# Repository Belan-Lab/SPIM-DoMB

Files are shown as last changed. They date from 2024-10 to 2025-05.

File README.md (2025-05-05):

Stand With Ukraine (https://stand-with-ukraine.pp.ua)

<p align="left">

</p>

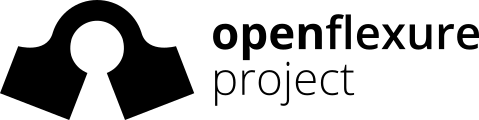
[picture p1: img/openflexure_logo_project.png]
OpenFlexure Project (https://gitlab.com/openflexure)


__SPIM for DoMB__
================

Selective Plane Illumination Microscope based on adaptations and modifications of original [openUC2](https://github.com/openUC2/UC2-GIT?tab=readme-ov-file) and [OpenFlexure Block Stage](https://gitlab.com/openflexure/openflexure-block-stage/) projects.

Department of Molecular Biophysics, Bogomoletz Institute of Physiology of NAS of Ukraine (Kyiv, Ukraine).

---

# Design notes

> [!TIP]
> Read more about the SPIM principles: 
>
> - [Selective Plane Illumination Microscopy](https://link.springer.com/chapter/10.1007/978-0-387-45524-2_37)
> - [openSPIM project](https://openspim.org/)
> - [Selective plane illumination microscopy techniques in developmental biology](https://journals.biologists.com/dev/article/136/12/1963/65234/Selective-plane-illumination-microscopy-techniques)
> - [Using tissue clearing and light sheet fluorescence microscopy for the three-dimensional analysis of sensory and sympathetic nerve endings that innervate bone and dental tissue of mice](https://onlinelibrary.wiley.com/doi/full/10.1002/cne.25582)

## Gaussian litgh-sheet
_Based on [Olarte et al., 2018](https://opg.optica.org/aop/fulltext.cfm?uri=aop-10-1-111&id=381035) and [Power and  Huisken, 2017](https://whttps://opg.optica.org/aop/fulltext.cfm?uri=aop-10-1-111&id=381035ww.nature.com/articles/nmeth.4224)._

__Schematic of the illumination and detection arm in a SPIM__ (_Olarte et al., 2018_)
<p align="center">
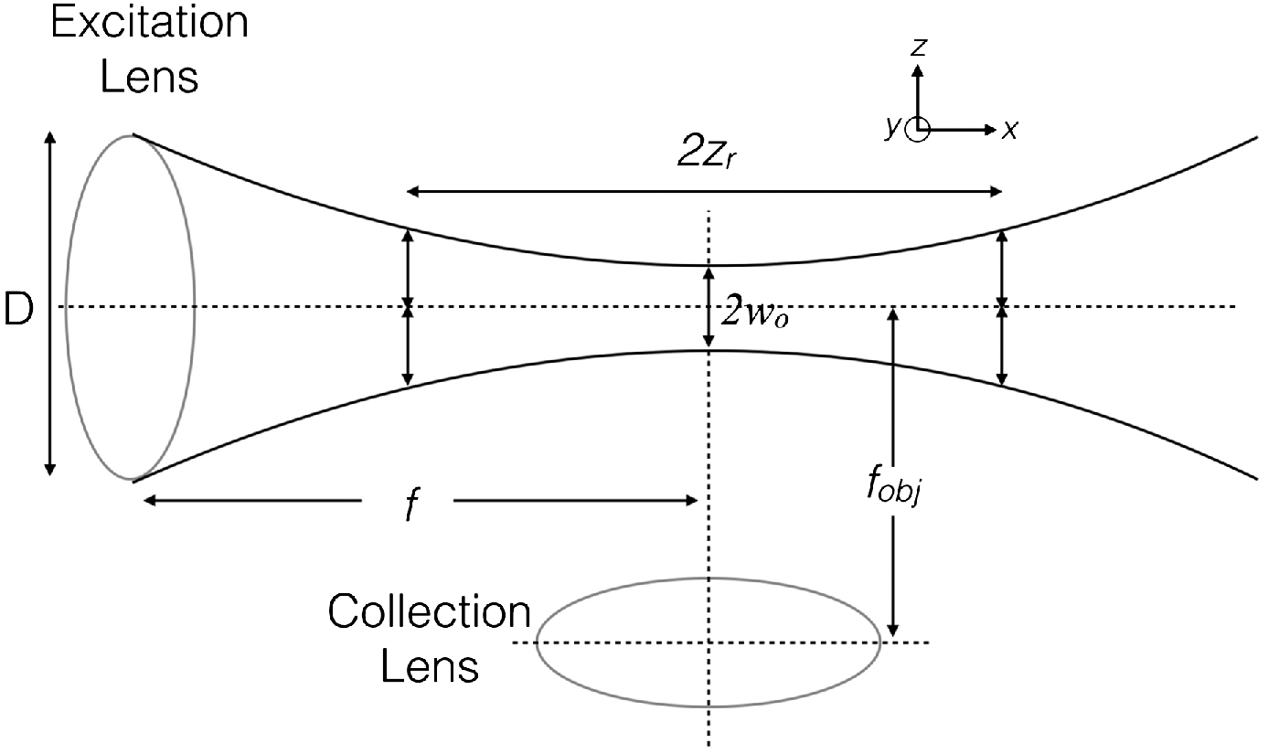
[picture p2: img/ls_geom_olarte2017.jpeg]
</a>
</p>

### Illumination arm
Light-sheet thickness (axial sectioning resolution): 

```math
l_z = 2w_0 = 2 \frac{n \cdot \lambda_{ex.}}{\pi \cdot NA_{ex.}}
```

Light-sheet length (field of view/FOV):

```math
l_x = 2z_r = 2 \frac{\pi \cdot w_0^2}{\lambda_{ex.}} = 2 \frac{n^2 \cdot \lambda_{ex.}}{\pi \cdot NA_{ex.}^2}
```

### Detection arm
Lateral resolution (Rayleigh criterion):

```math
d_{xy} = \frac{0.61 \cdot \lambda_{det.}}{NA_{det.}}
```

Axial resolution (depth of field/DOF):

```math
d_z = \frac{n \cdot \lambda_{det.}}{NA_{det.}^2}
```

# Samples and desired characteristics

__NB: is 10x NA 0.25 FN 22 enough?__

## Sciatic nerve
- Nerve diameter: 1.5-2 mm
- Nerve length: 5-20 mm
- A-fiber diameter: 1.5 - 10 um 
- C-fiber diameter: 0.5 - 2 um
- Minimal vessel diameter

## Scaffolds
_In progress_

# Relation of components and parameters
## Objectives

| Model                           | Olympus PlaN | Olympus UPlanFl Ph. 1 |
| ------------------------------- | ------------ | --------------------- |
| Magnification (M)               | 10x          | 10x                   |
| Numerical aperture (NA)         | 0.25         | 0.3                   |
| Working distance (WD)           | 10.6 mm      | 10 mm                 |
| Focal distance (F)              | 18 mm        | 18 mm                 |
| Back focal plane distance (BFP) | N/A          | -19.1 mm              |
| Field number (FN)               | 22           | 26.5 mm               |
| Lateral resolution              | 1.34 μm      | 1.12 μm               |
| Parafocal distance (PD)         | 45 mm        | 65 mm                 |
| Exit pupil diameter (EP)        | 9 mm         | 10.8 mm               |

## Cameras

| Model           | FLIR Grasshopper 3     | Basler ace 2 R       |
| --------------- | ---------------------- | -------------------- |
| ID              | GS3-U3-23S6M-C         | a2A5320-23umPRO      |
| Sensor          | Sony IMX174 (CMOS)     | Sony IMX542 (CMOS)   |
| Sensor size     | 11.25x7.03 mm (1/1.2") | 14.58x8.31 mm (1.1") |
| Sensor diagonal | 13.4 mm                | 16.78 mm             |
| Pixels (HxV)    | 1920x1200 (2.3 Mpx)    | 5320x3032 (16.1 Mpx) |
| Pixel size      | 5.86x5.85 μm           | 2.74x2.74 μm         |
| Frame rate      | up to 162 fps          | up to 24 fps         |

---

# T-SPIM 
Here will be construction notes for the next project, T-SPIM extension of DoMB-SPIM.

## Design overview, V0

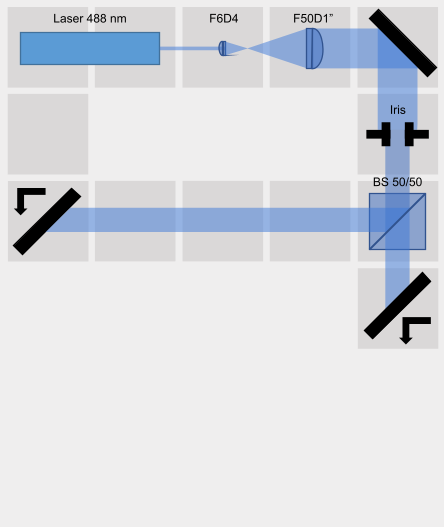
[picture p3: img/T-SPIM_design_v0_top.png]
| Top layer        |     |
| :--------------: | :----------------------------------: |
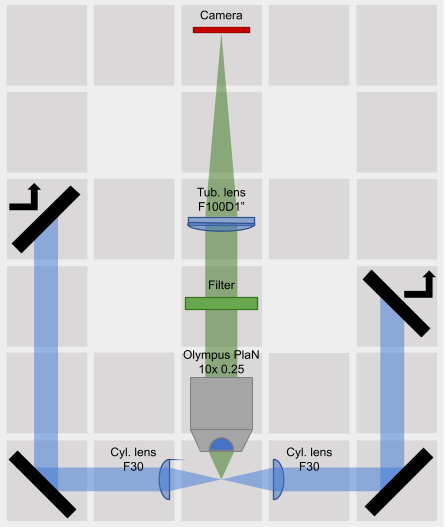
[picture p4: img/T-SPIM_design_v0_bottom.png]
| __Bottom layer__ |  |

---

# L-SPIM

## Microscope configuration
<p align="center">
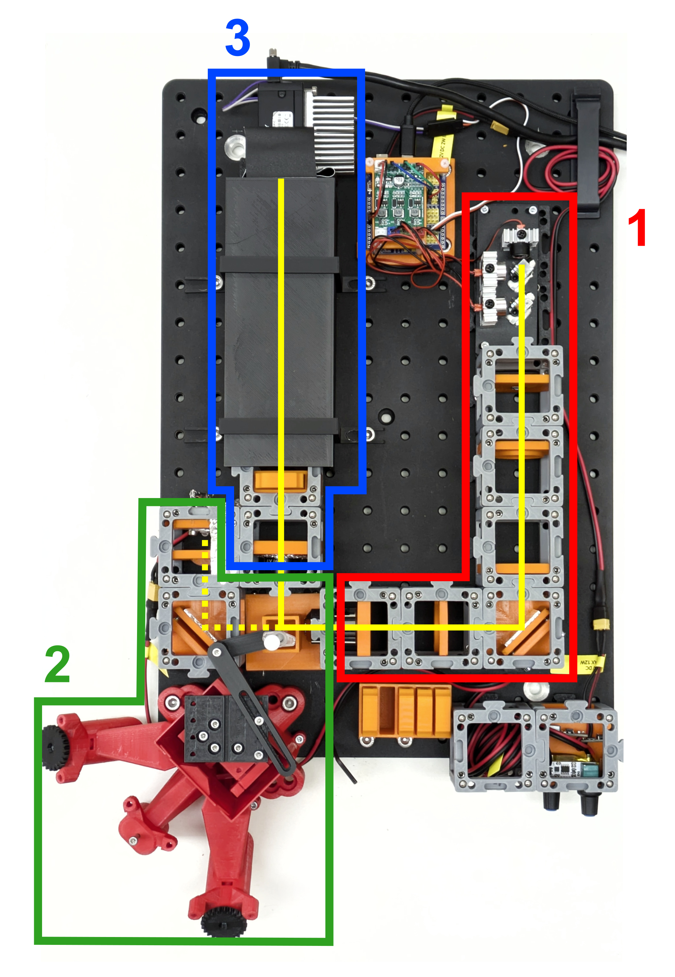
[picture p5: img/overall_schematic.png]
</a>
</p>

The microscope consists of three main parts: (__1__) excitation light path with a light source, light source control board, and light sheet collimation system, (__2__) sample handling part which includes a sample chamber with modified OpenFlexure Block Stage and side illumination system, and (__3__) detection light path with emission filter, tube lens, and industrial-grade CMOS camera ([FLIR Grasshopper 3](https://www.edmundoptics.com/p/gs3-u3-23s6m-c-112-grasshopper-usb-30-monochrome-camera/30859/?srsltid=AfmBOor05Spkup9nlj1Yhpo8lcCk5ABTsBXECeMxt9GTolSTdF2UEIqc) in our case). A solid yellow line indicates the excitation and detection light path, and a dashed yellow line indicates the brightfield side-illumination light path. 

The whole setup is based on on-shelf parts and low-cost solutions with minimal additional modifications. For all 3D-printed parts, parametric openSCAD models were provided for flexible modification and customization without a great entry threshold.  

This system is under strong development, so check for future updates.

## First results

__Light sheet configuration__
 Light sheet top view | Light sheet side view | Light sheet focus point view 
:-------------------------:|:-------------------------:|:-------------------------:
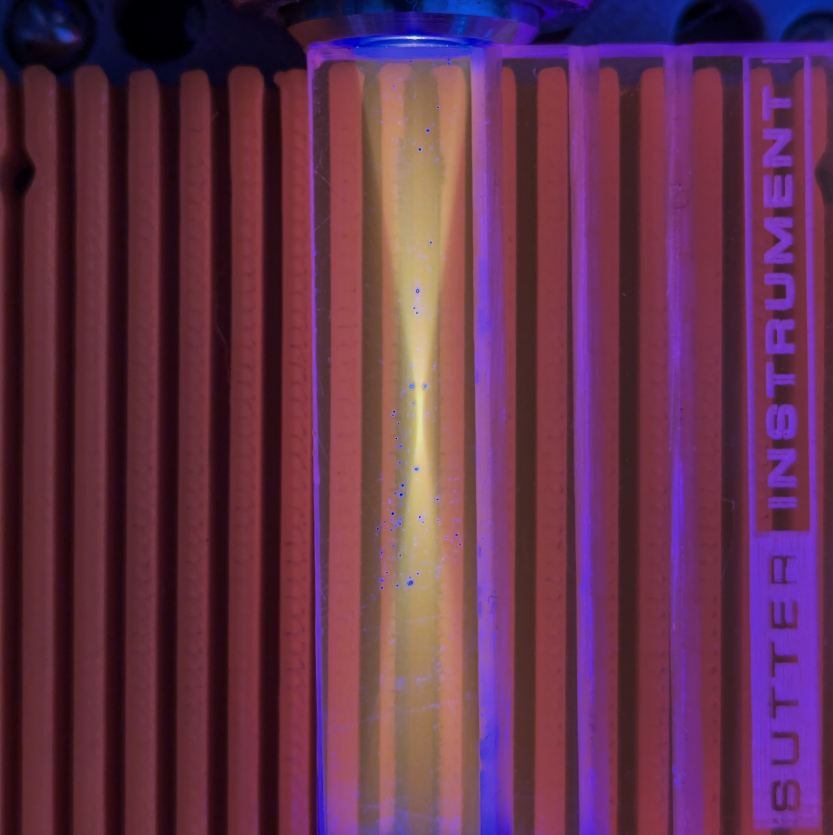
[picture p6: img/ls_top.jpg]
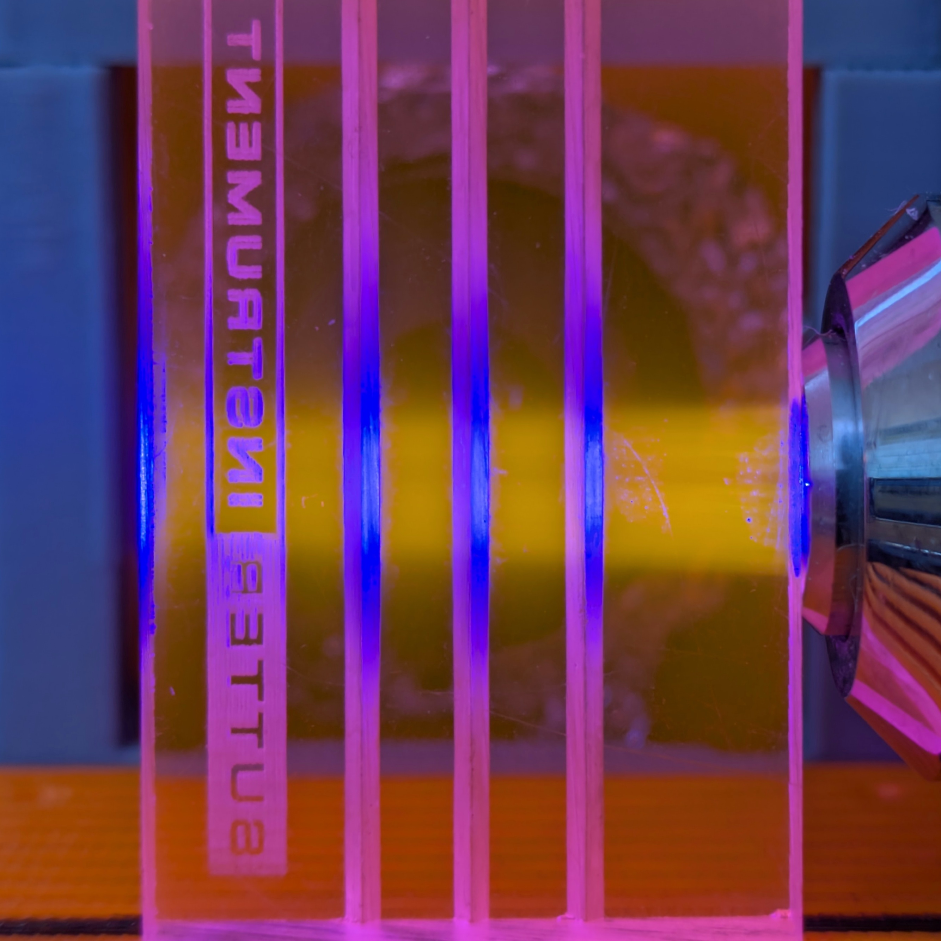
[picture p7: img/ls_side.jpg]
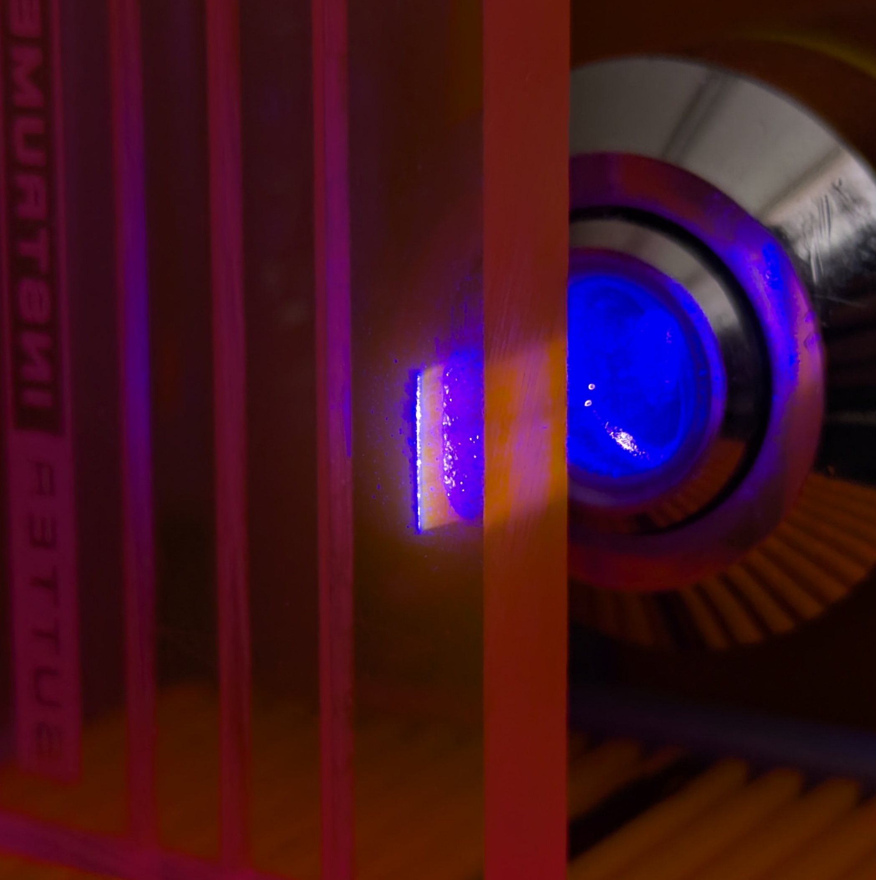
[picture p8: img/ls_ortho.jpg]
||  

__Z-stack and reconstruction of whole mount staining of vessels endothelial cells in the sciatic nerve__

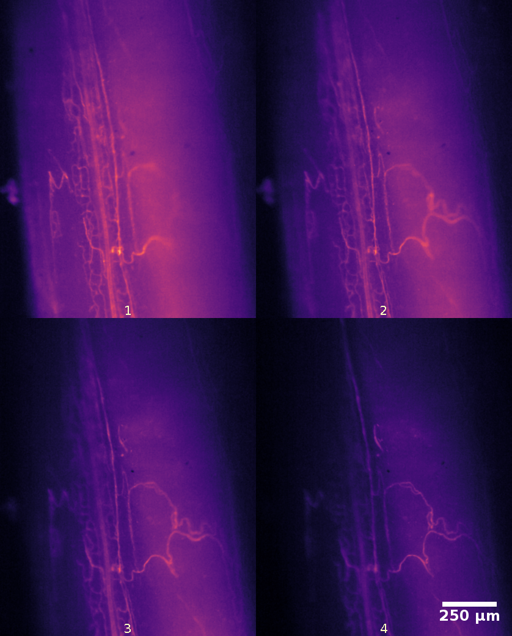
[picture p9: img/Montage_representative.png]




## Construction notes
General materials and parts needed for printing and assembling:

| Part                               | #     | Cost/unit | Link                                                         |
| ---------------------------------- | ----- | --------- | ------------------------------------------------------------ |
| Optical breadboard 30x45 cm        | 1x    | $135      | [AliExpress](https://a.aliexpress.com/_EwQ40qd)              |
| M3x12 DIN912 screw                 | ~200x | ~$8 / 200 | Metalvis                                                     |
| M6x12 DIN912 screw                 | ~30x  | ~$6 / 30  | Metalvis                                                     |
| M6x12 DIN912 screw                 | ~10x  | ~$1 / 10  | Metalvis                                                     |
| M5x8 DIN914 screw                  | ~150x | ~$5 / 150 | Metalvis                                                     |
| 1.75 mm PLA filament (750 g/pack)  | 2x    | $11       | [Monofilament](https://monofilament.com.ua/ua/products/standartnye-materialy/pla/pla-cvetlo-seryj-o1-75mm-ves0-75kg) |
| 1.75 mm ABS+ filament (750 g/pack) | 1.5x  | $10.85    | [Monofilament](https://monofilament.com.ua/ua/products/standartnye-materialy/abs-plus/abs-plus-oranzhevyj) |
| __Total__                          |       | __~$200__ |                                                              |

## 1. Excitation light path

<p align="center">
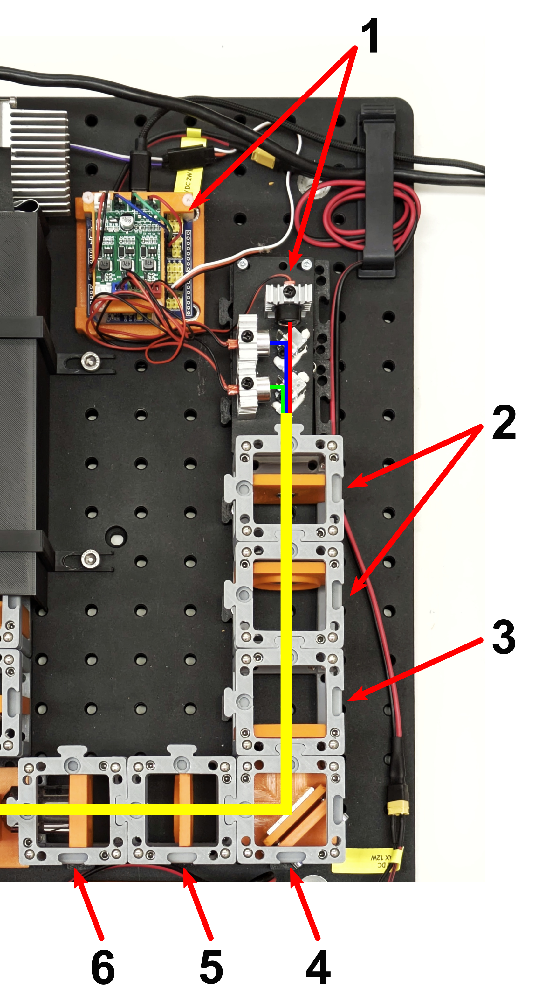
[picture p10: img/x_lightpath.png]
</a>
</p>

1. [RGB lasers module and lasers trigger board](#rgb-laser-module-v0)
2. ~12x beam expander: iPhone 4S lens F3.85 and F50 lens
3. Cylinrical lens F30
4. 45° kinematic mirror
5. Focusing lens F50
6. Projection objective 10x NA 0.25

| Part                                      | #    | Cost/unit | Link                                            |
| ----------------------------------------- | ---- | --------- | ----------------------------------------------- |
| [RGB lasers module](#rgb-laser-module-v0) | 1x   | $23       |                                                 |
| iPhone 4S lens F3.85                      | 1x   | -         |                                                 |
| F50 D30 lens                              | 2x   | $0.68     | [AliExpress](https://a.aliexpress.com/_ExOjTDP) |
| F30 20x22 mm cylindrical lens             | 1x   | $10.54    | [AliExpress](https://a.aliexpress.com/_EuDzlJ3) |
| Fron surface mirror 30x30 mm              | 1x   | $1.46     | [AliExpress](https://a.aliexpress.com/_EHn0u2l) |
| 10x NA 0.25 infinity corrected objective  | 1x   | $15.54    | [AliExpress](https://a.aliexpress.com/_ExDrPj7) |
| __Total__                                 |      | __~$52__  |                                                 |

## 2. Sample handling

<p align="center">
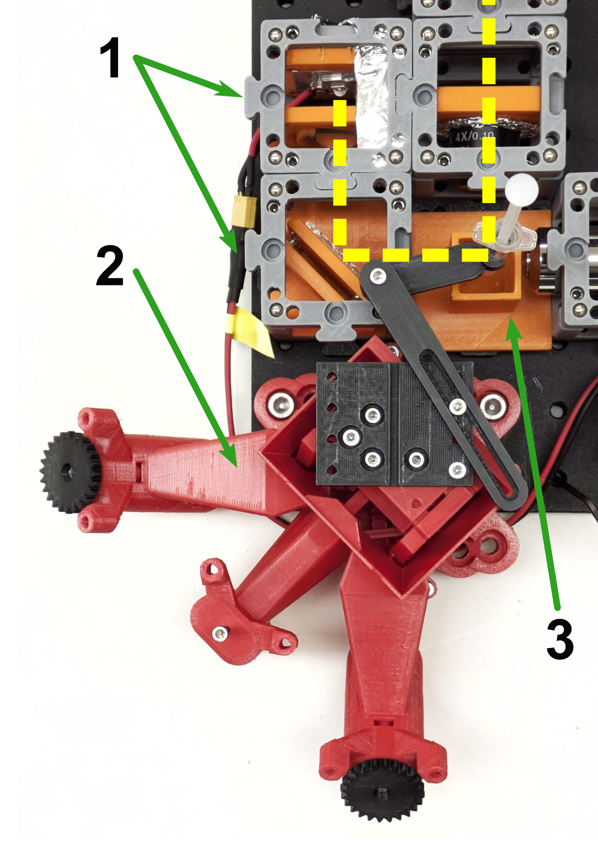
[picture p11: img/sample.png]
</a>
</p>

1. [White LED 3.3V 10W](#led-and-power-cube-v0) and 45° kinematic mirror
2. [OpenFlexure Block Stage with sample holder](#openflexure-block-stage-and-sample-holder)
3. [Sample chamber](#sample-chamber-v0)

| Part                                         | #    | Cost/unit | Link                                            |
| -------------------------------------------- | ---- | --------- | ----------------------------------------------- |
| [LED and power cube](#led-and-power-cube-v0) | 1x   | $12.68    |                                                 |
| Fron surface mirror 30x30 mm                 | 1x   | $1.46     | [AliExpress](https://a.aliexpress.com/_EHn0u2l) |
| __Total__                                    |      | __~$14__  |                                                 |

## 3. Detection light path

<p align="center">
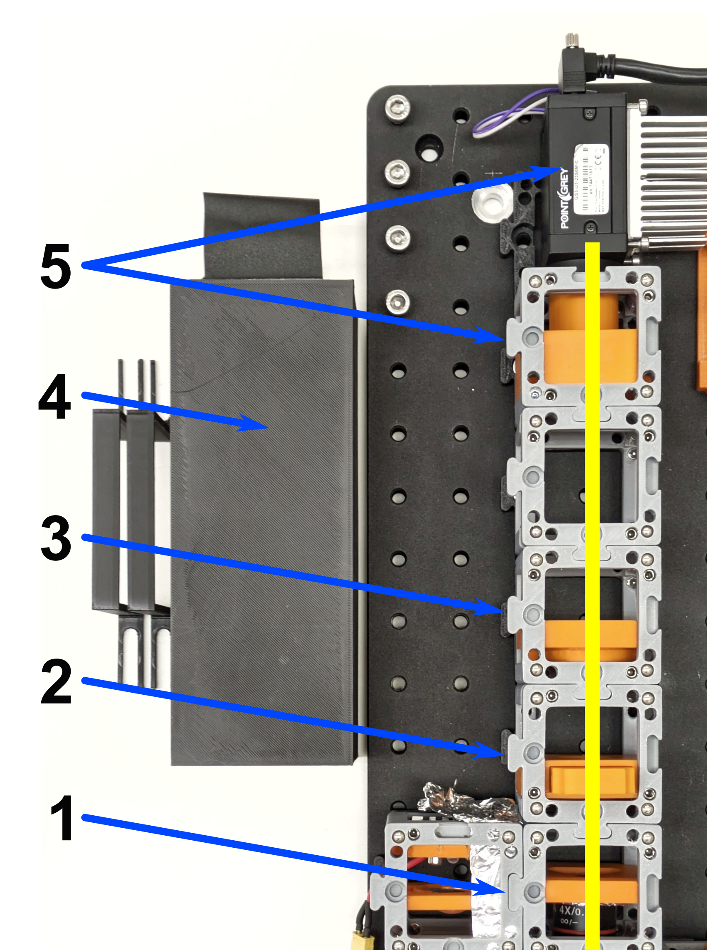
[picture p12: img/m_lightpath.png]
</a>
</p>

1. Objective 4x NA 0.1
2. [Emission filter holder](#25-mm-filter-holder-v1)
3. Tube lens ~F180
4. Light protection enclosure
5. CMOS camera and [C-mount cube](#c-mount-adapter)

| Part                                   | #    | Cost/unit                                  | Link                                                         |
| -------------------------------------- | ---- | ------------------------------------------ | ------------------------------------------------------------ |
| 4x NA 0.1 infinity corrected objective | 1x   | $13.25                                     | [AliExpress](https://a.aliexpress.com/_ExDrPj7)              |
| 25 mm emission filter                  | 1x   | discontinued old filter set, but new >$300 |                                                              |
| F~180 D40 lens                         | 1x   | from old stereomicroscope                  |                                                              |
| FLIR Grasshopper 3                     | 1x   | $1179                                      | [Edmund Optics](https://www.edmundoptics.com/p/gs3-u3-23s6m-c-112-grasshopper-usb-30-monochrome-camera/30859/?srsltid=AfmBOor05Spkup9nlj1Yhpo8lcCk5ABTsBXECeMxt9GTolSTdF2UEIqc) |
| __Total__                              |      | __~$1195__                                 |                                                              |

> [!IMPORTANT]
>
> The cost of the entire microscope, excluding the CMOS camera and emission filters set, was less than $300. A possible alternative for expensive emission filters may be industrial-grade filters for multimedia projector systems, but with a minimal selection of possible passbands. I also recommend paying attention to other manufacturers of industrial monochrome cameras: [Allied Vision](https://www.alliedvision.com/en/products/camera-series/alvium-1800-u/), [Basler](https://www.baslerweb.com/en/cameras/?srsltid=AfmBOooR76UWs6U6YJbZBzX9LeqmtPnLls9piX8MenW-n_NOVcxJU0dT), [Daheng](https://en.daheng-imaging.com/list-2-1.html).

---

# Cubes and modules
## OpenFlexure Block Stage for SPIM

Active development of OpenFlexure Block Stage adaptation continues on a separate [repository](https://github.com/Belan-Lab/OpenFlexure-XYZR).

__Block Stage side view__
<p align="center">
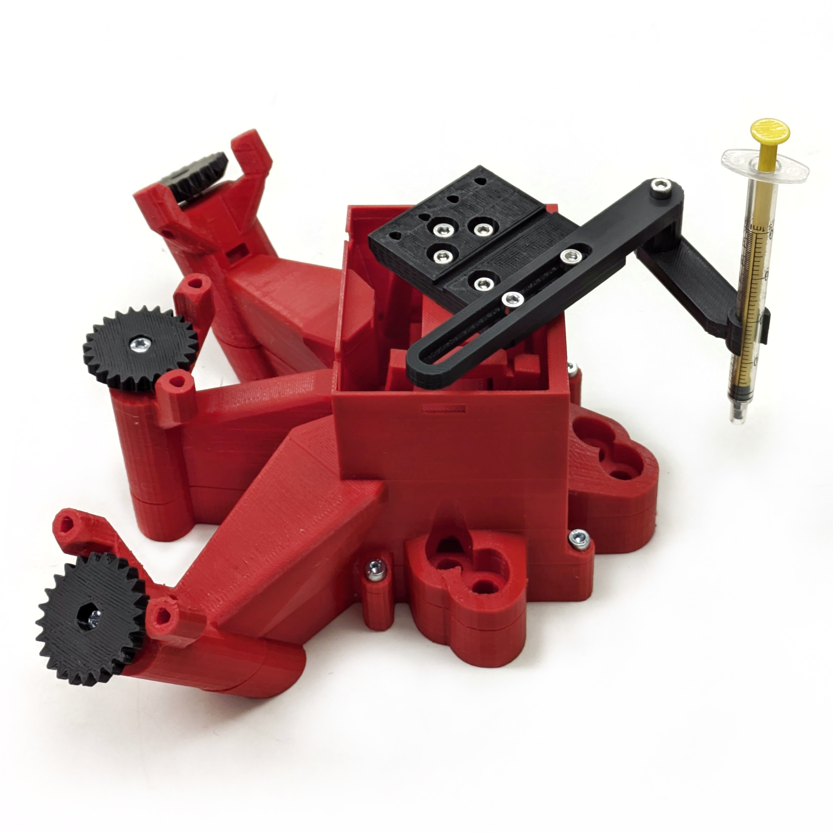
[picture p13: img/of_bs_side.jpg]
</a>
</p>

## C-mount adapter
Parametric model of a cube insert with C-mount thread (_c-mount_insert_v0.scad_).

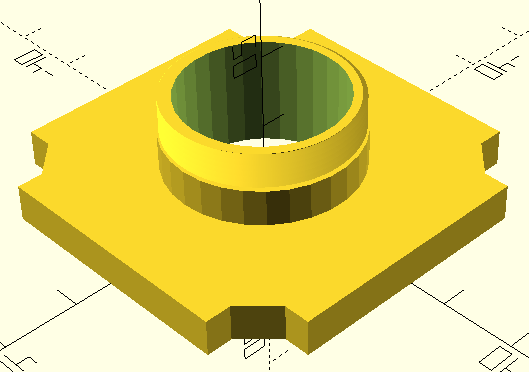
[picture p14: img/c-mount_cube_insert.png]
Model         | 
:-------------------------:|:-------------------------:
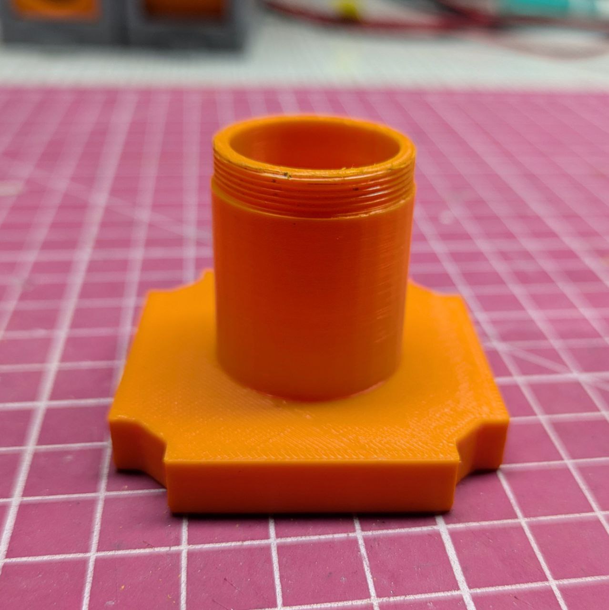
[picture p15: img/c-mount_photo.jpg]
__Printed long insert__ | 
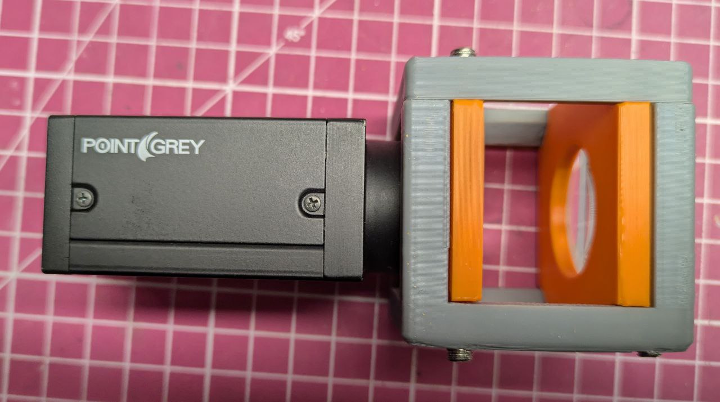
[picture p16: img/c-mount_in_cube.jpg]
__Installed insert__| 

##  LED and power cube V0
Parametric model of a cube insert with two LED dimmers and 12V output with type-C Power Delivery input (_led_power_insert_v0.scad_).

__Model__

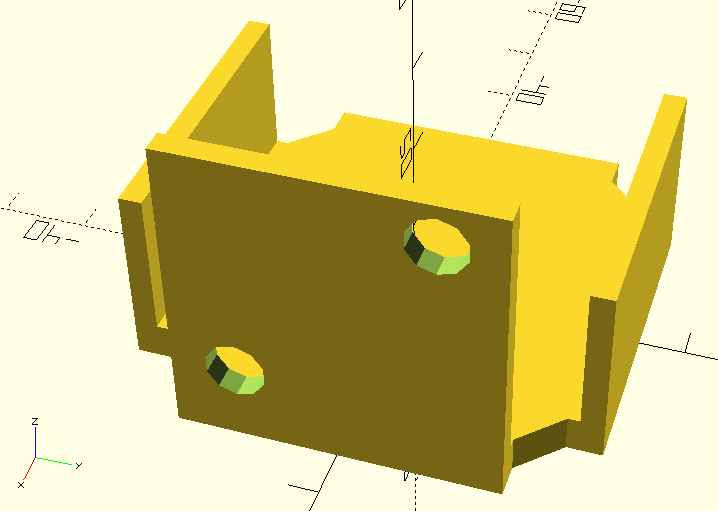
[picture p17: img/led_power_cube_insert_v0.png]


Part|#|Cost/unit|Link
-|-|-|-
LED dimmer | 2x | $2.72   | [AliExpress](https://a.aliexpress.com/_EuX3DTP) 
PD decoy module 12V | 1x | $0.44   | [AliExpress](https://a.aliexpress.com/_Ezeg4Hf) 
Mini560 Pro Step Down to 3.3V| 1x | $0.81  | [AliExpress](https://a.aliexpress.com/_EJQFP5x) 
White LED 10W 3.3V (XML2) | 1x | $1.29  | [AliExpress](https://a.aliexpress.com/_EHBMyXT) 
460 nm LED 3W 3.3V | 1x | $0.2 | [AliExpress](https://a.aliexpress.com/_EI94HWN)
Acrilic LED lens, F22 D20.8 | 2x | $1.35 | [AliExpress](https://a.aliexpress.com/_EHJOUo1) 
XT30 connector | 3x | $0.6  | [arduino.ua](https://arduino.ua/prod5276-xt30-konnektor-para-dlya-podklucheniya-li-po-li-ion-akkymylyatorov)
__Total__ |  | __$12.68__ | 

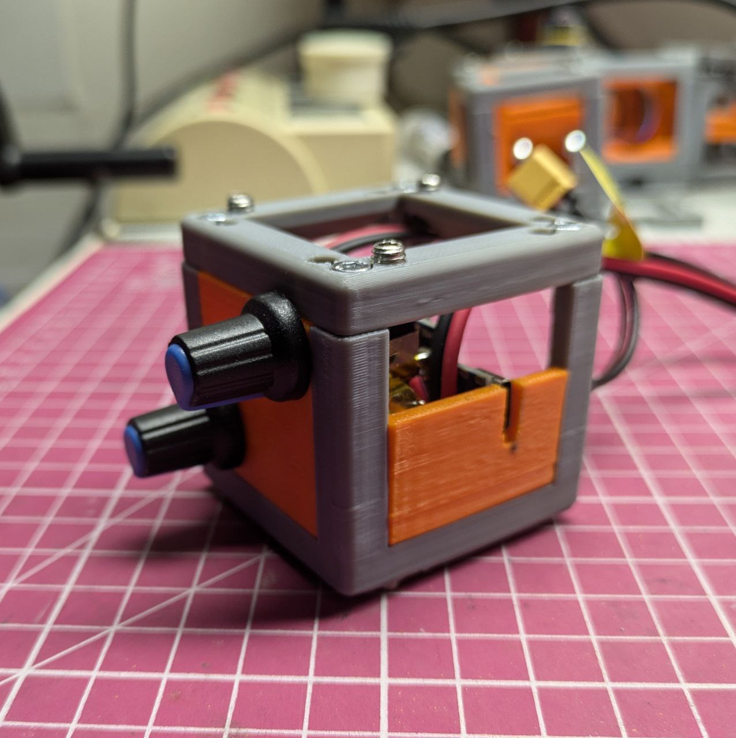
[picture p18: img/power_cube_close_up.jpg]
Assembled power cube            | 
:-------------------------:|:-------------------------:
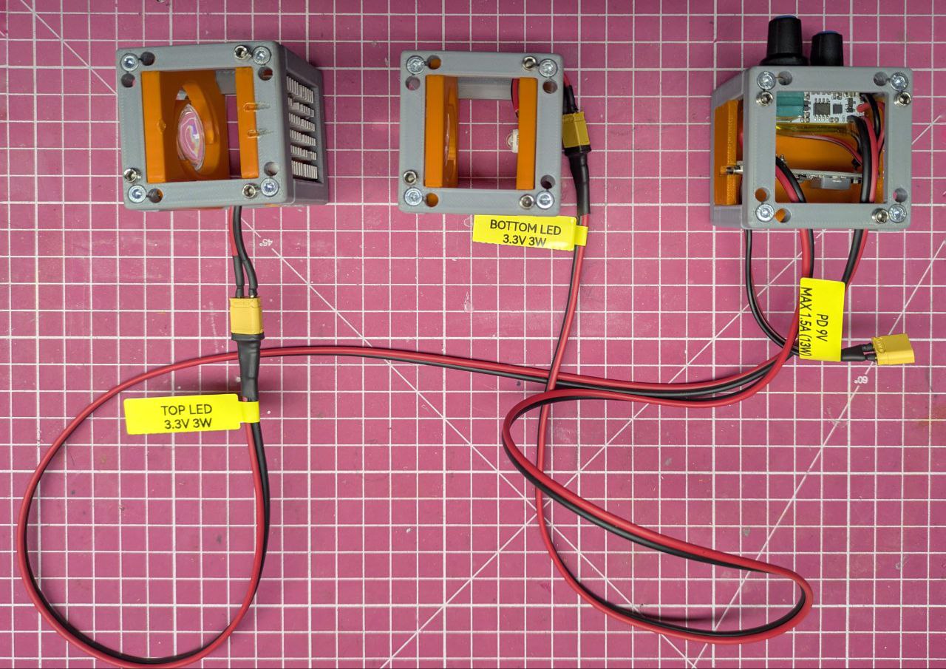
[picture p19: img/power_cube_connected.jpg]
__Power cube with two LED cubes__ | 

__White 10W LED cube with radiator from northbridge__

Front view            |  Back view
:-------------------------:|:-------------------------:
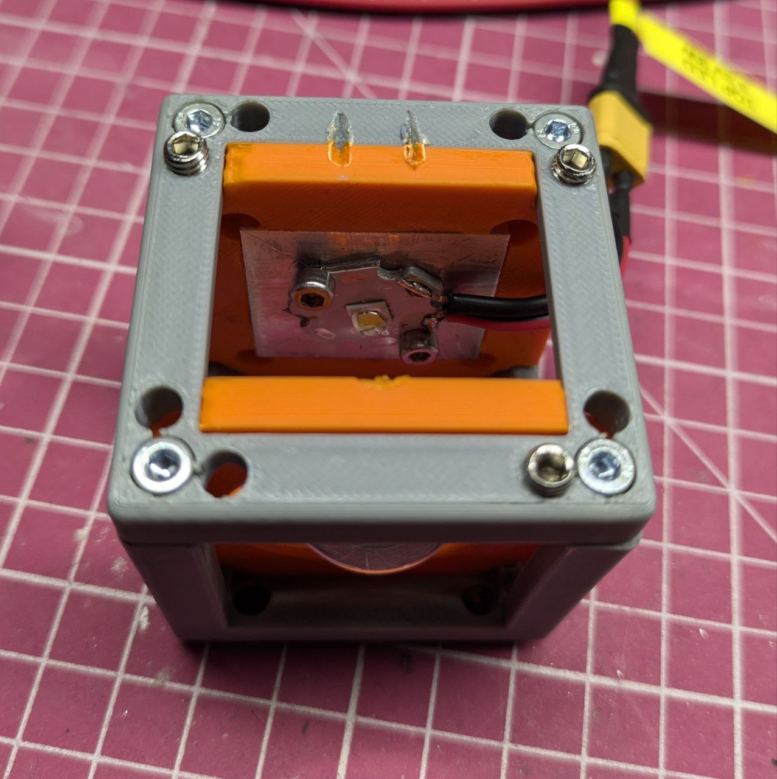
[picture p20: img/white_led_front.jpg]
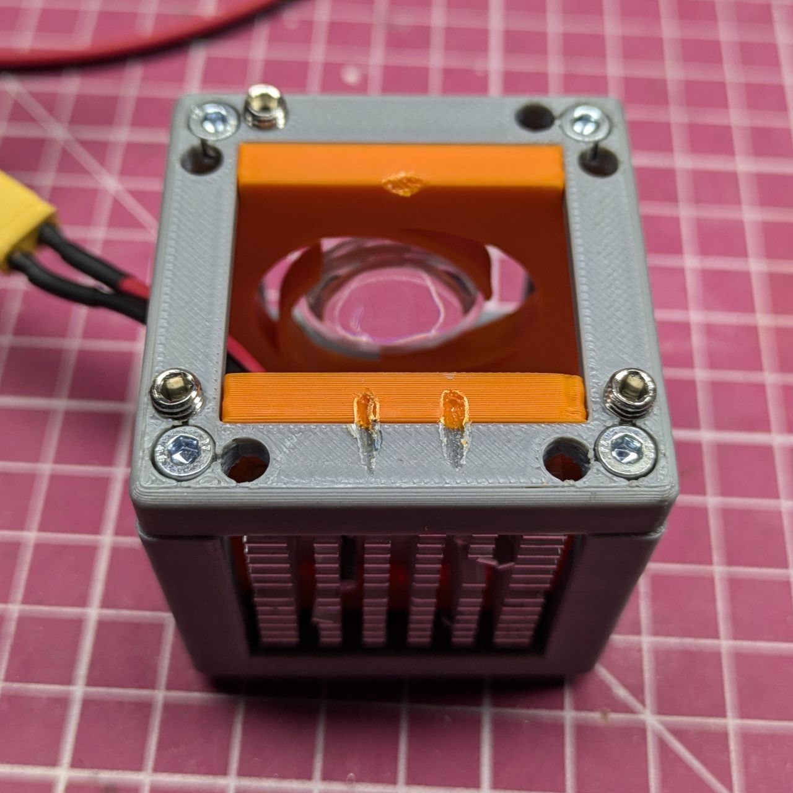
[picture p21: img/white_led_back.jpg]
 | 

## 25 mm filter holder V1
Sliding holder for standard 25 mm optical filters. The storage box for filter holders has mounting holes for standard M6 25mm spacing optical board.

__Model__

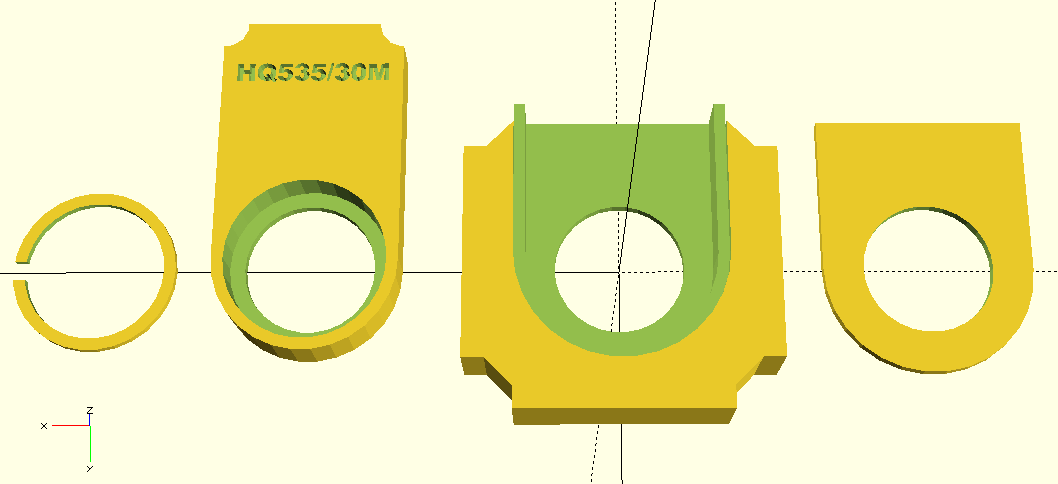
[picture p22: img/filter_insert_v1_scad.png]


Assembled filter cube             | Filter cube with filter holders and holders storage box 
:-------------------------:|:-------------------------:
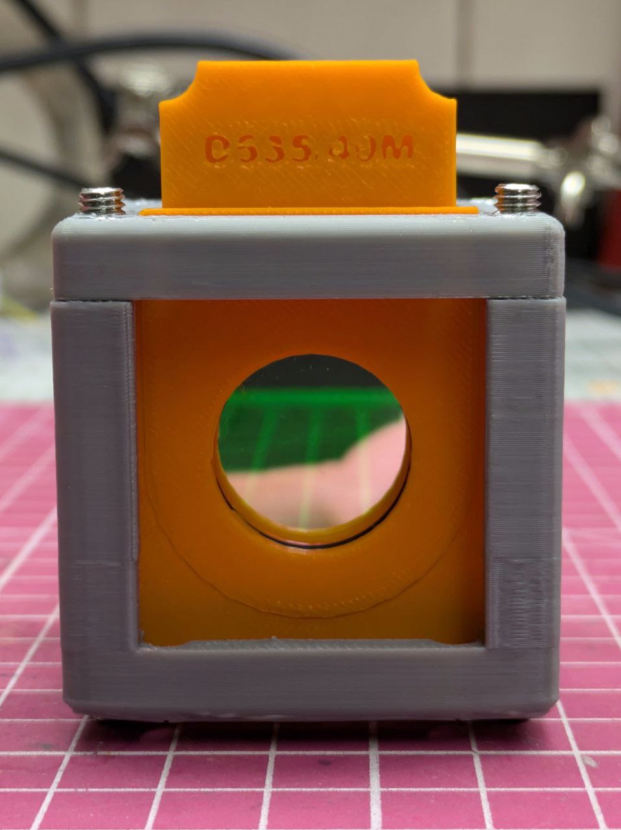
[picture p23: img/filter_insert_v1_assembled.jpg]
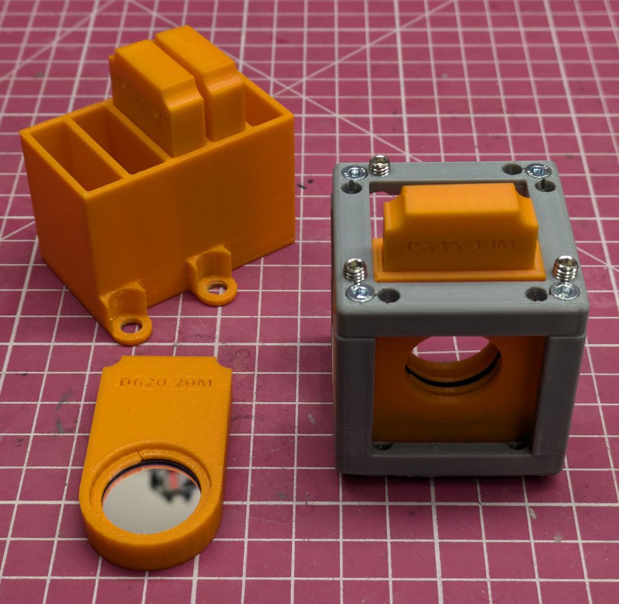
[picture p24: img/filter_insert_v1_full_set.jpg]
 | 

## Sample chamber V0
Sample chamber with three glass walls, as chamber windows was used 18 mm diameter 0.18 mm thickness coverslips mounted on silicone sealant.

Model           |  Assembled chamber
:-------------------------:|:-------------------------:
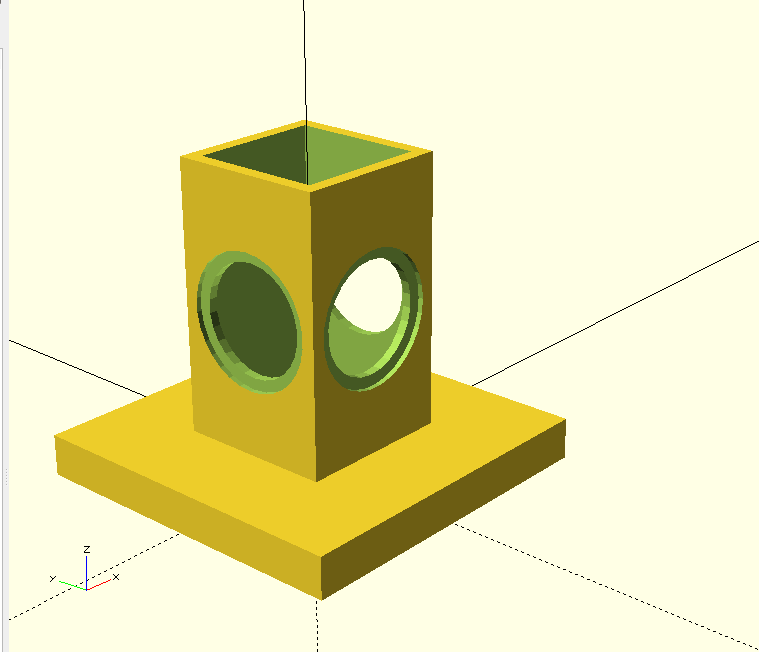
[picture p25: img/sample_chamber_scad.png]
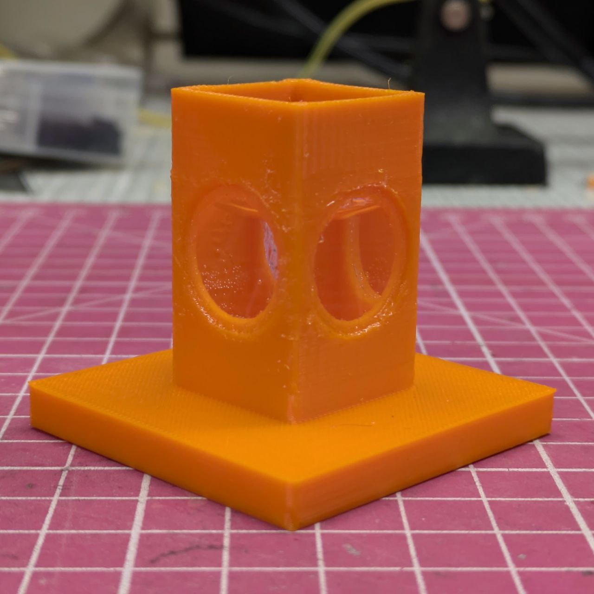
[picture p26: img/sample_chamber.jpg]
 | 

## Servo stage V1
The holder was adapted to install a plastic photometric cuvette for sample mounting.

__Model__
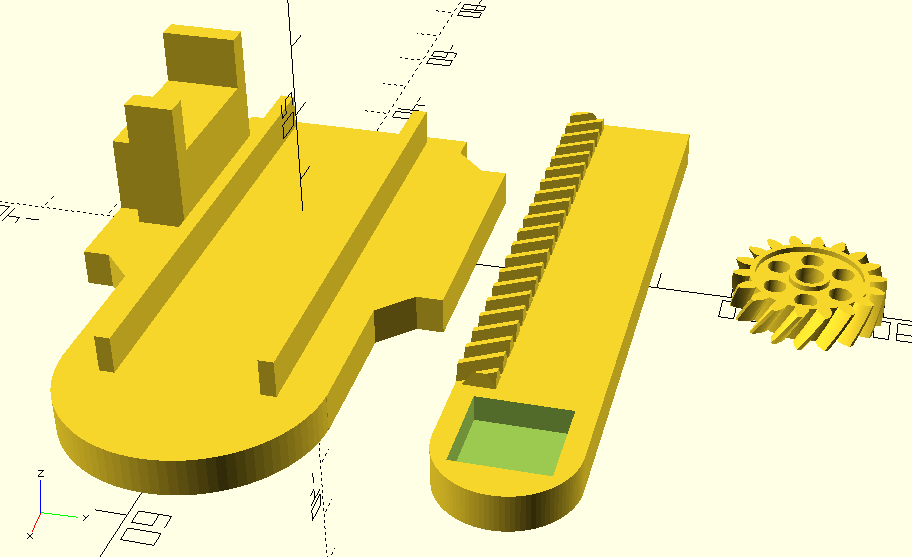
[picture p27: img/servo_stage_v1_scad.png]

_Includes openSCAD library "Bibliothek für Evolventen-Zahnräder, Schnecken und Zahnstangen" (gear.scad)_

__Assembled cube__

Top view            |  Side view
:-------------------------:|:-------------------------:
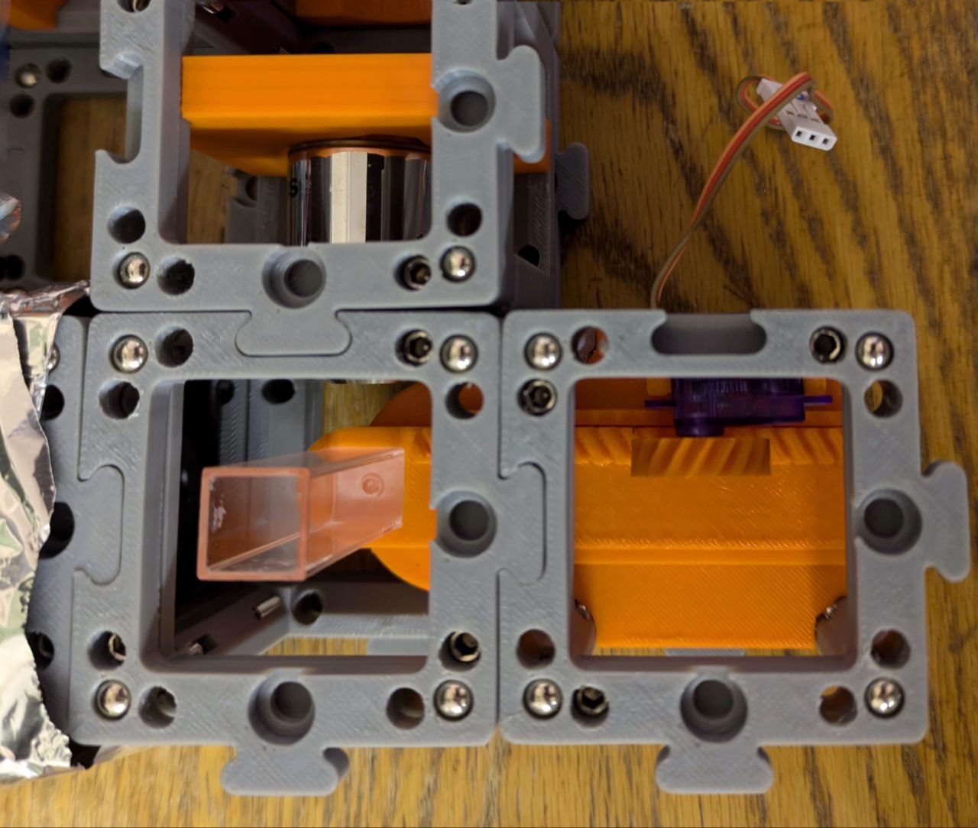
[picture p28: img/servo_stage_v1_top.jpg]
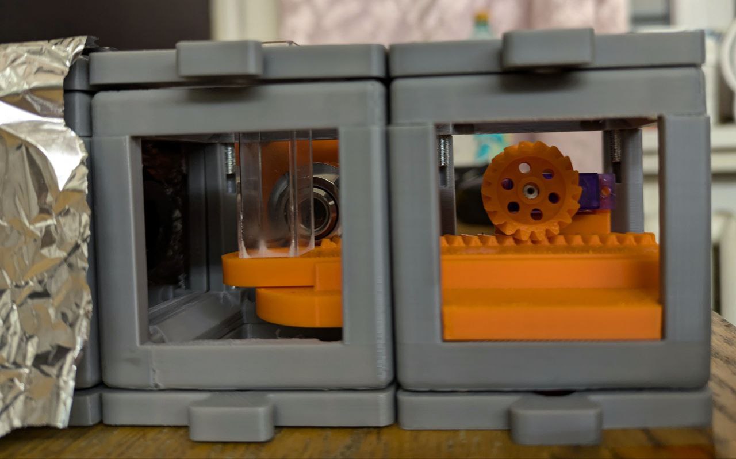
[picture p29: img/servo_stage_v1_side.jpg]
 | 

## 5X Laser beam expander V0

__Model__

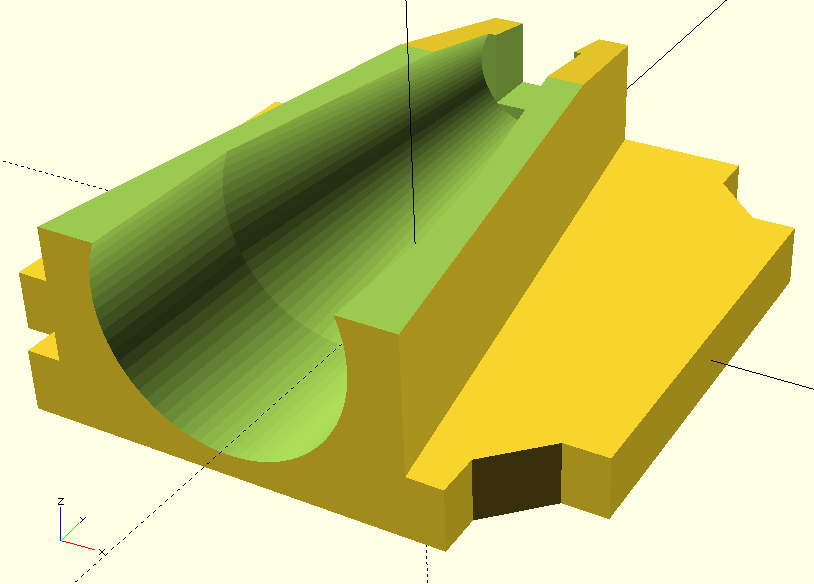
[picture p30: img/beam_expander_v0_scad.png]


Part|#|Cost/unit|Link
-|-|-|-
Acrilic LED lens, F22 D20.8 | 1x | $1.35 | [AliExpress](https://a.aliexpress.com/_EHJOUo1) 
iPhone 4S lens, F3.85 | 1x |  -  |  

## RGB lasers module V0

Module for mounting and control with Arduino of the RGB laser LED module.

Part|#|Cost/unit|Link
-|-|-|-
RGB laser module | 1x | $19.5 | [AliExpress](https://a.aliexpress.com/_EHowiiN)
Arduino Nano compatible board | 1x | $2.13 | [AliExpress](https://a.aliexpress.com/_EwrjzyD) 
Arduino Nano expansion board | 1x | $0.94 | [AliExpress](https://a.aliexpress.com/_EyNqegd) 
PD decoy module 12V | 1x | $0.44 | [AliExpress](https://a.aliexpress.com/_Ezeg4Hf) 
__Total__ |  | __$23__ |  

__RGB laser trigger board modification__

The original diode bridge on the RBG laser trigger board (circled in red) was replaced with two jumpers for the DC power supply only, and the original trigger connectors were replaced with 2.54 mm pin headers.

Original board             |  Modified board
:-------------------------:|:-------------------------:
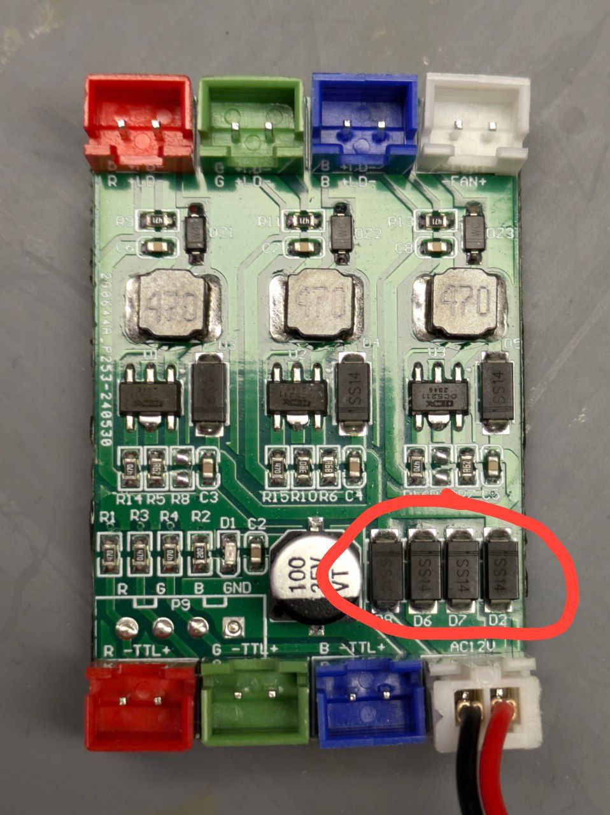
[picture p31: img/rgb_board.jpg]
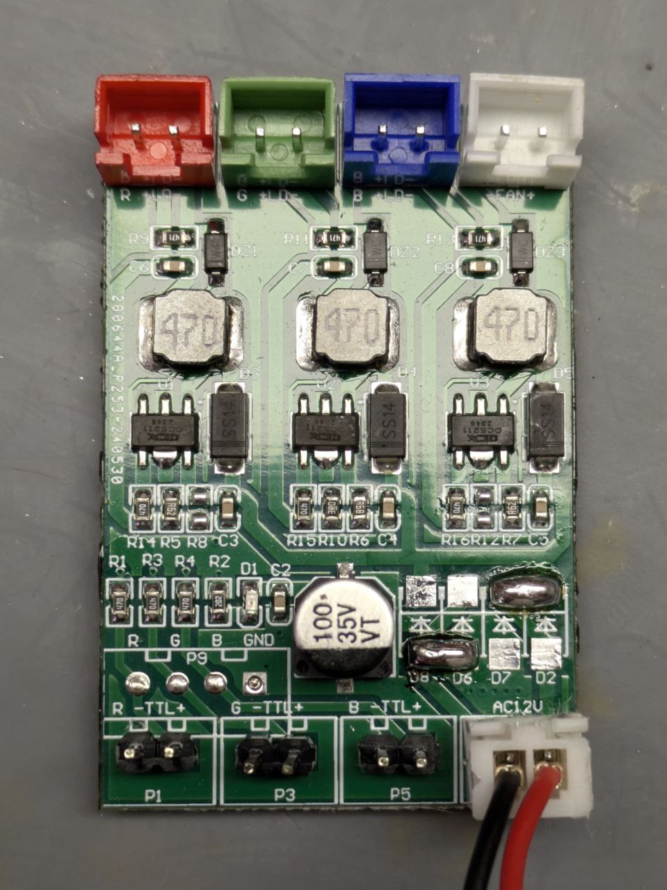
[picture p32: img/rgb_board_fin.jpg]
 | 

__Nano expansion board modification__

The expansion board's original DC connector (circled in red) was replaced with a PD trigger module for power supply with a power delivery source (AC adapter, power bank, etc.).

Original board (top)            |  Modified board (top)
:-------------------------:|:-------------------------:
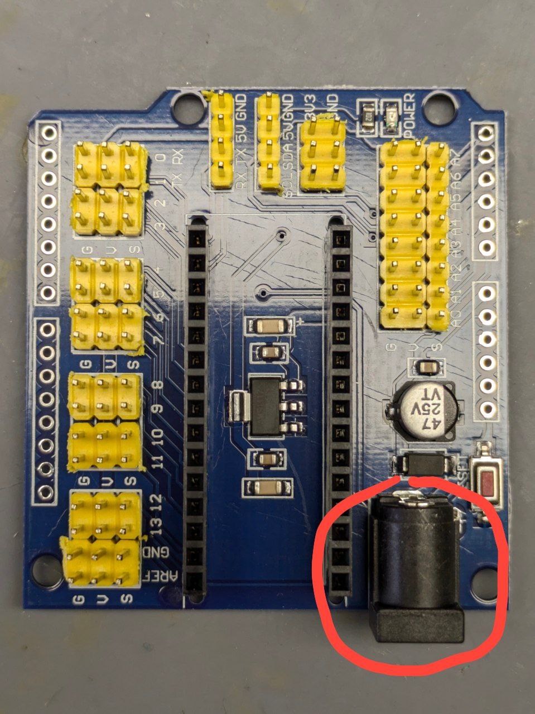
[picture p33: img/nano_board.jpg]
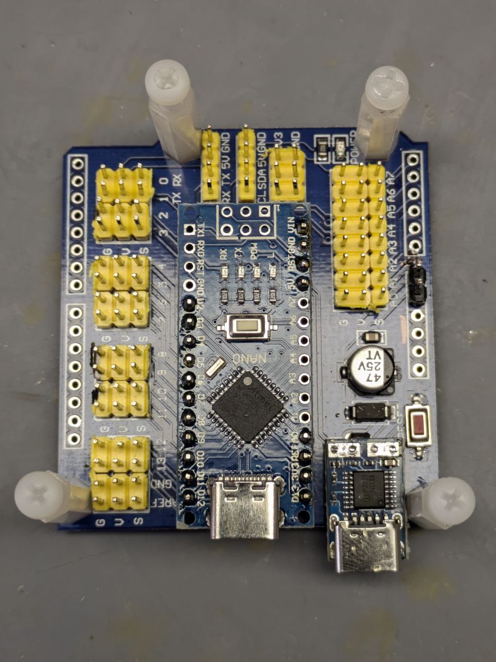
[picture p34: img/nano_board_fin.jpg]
 | 

Arduino pin 2 was pulled up with a 1K resistor to the 5V (circled in red) for connection to the passive trigger output of the Point Grey Grasshopper 3 camera (trigger output - pin 2, gnd - pin 6). The male XT30 connector for an optional power supply from the LED/power cube was soldered to the power input. 

Original board (bottom)            | Modified board (bottom) 
:-------------------------:|:-------------------------:
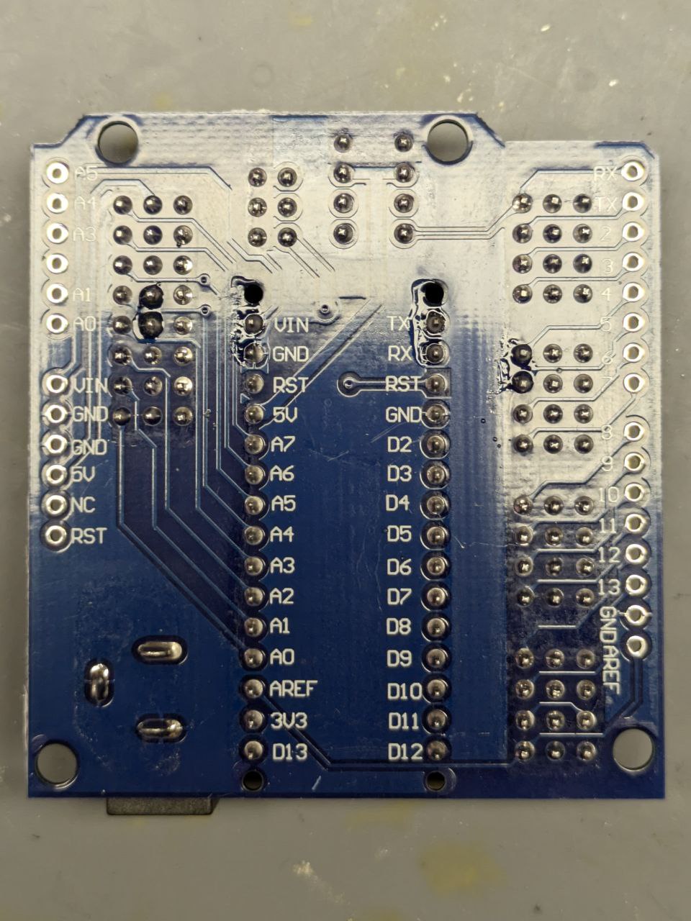
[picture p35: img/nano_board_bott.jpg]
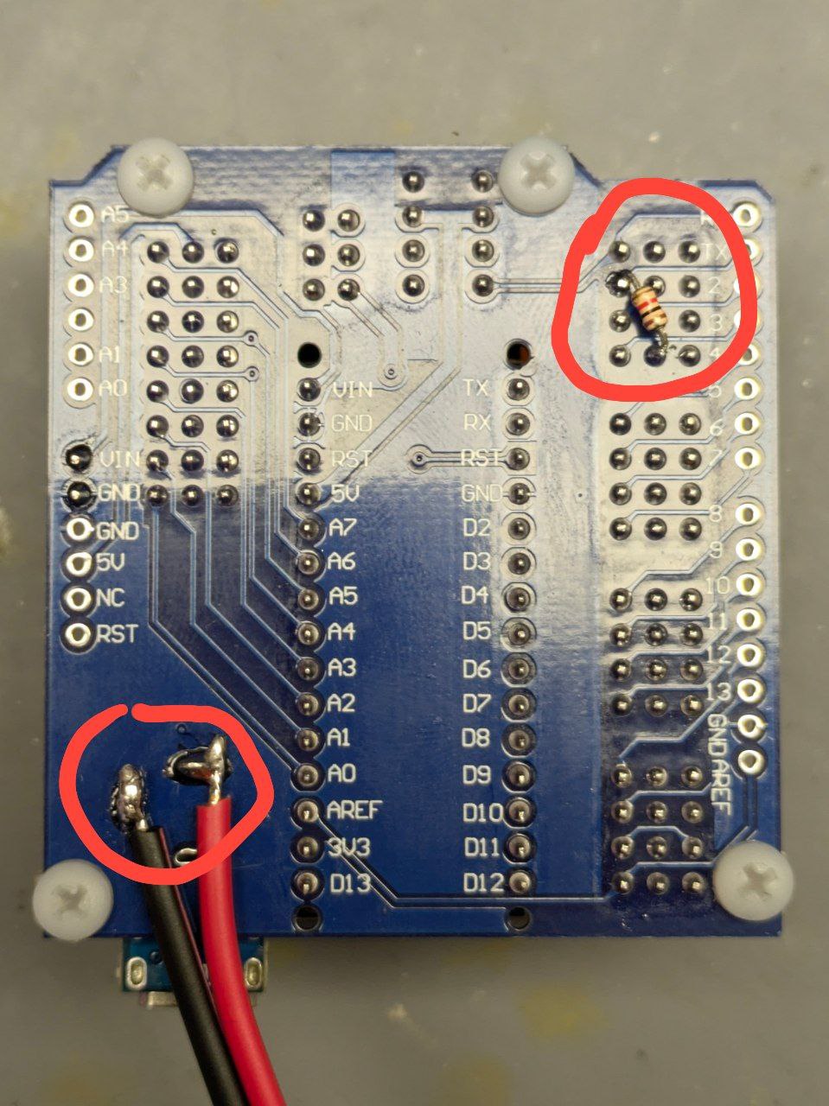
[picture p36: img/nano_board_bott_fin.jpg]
 |  

__Assembled control module__

Lasers powered through an arduino Vin pin.

TTL inputs of the RGB laser trigger board  was connected to the next arduino pins:

- __650 nm__ - 8
- __520 nm__ - 9
- __450 nm__ - 10

Trigger board holder  | Assembled module 
:-------------------------:|:-------------------------:
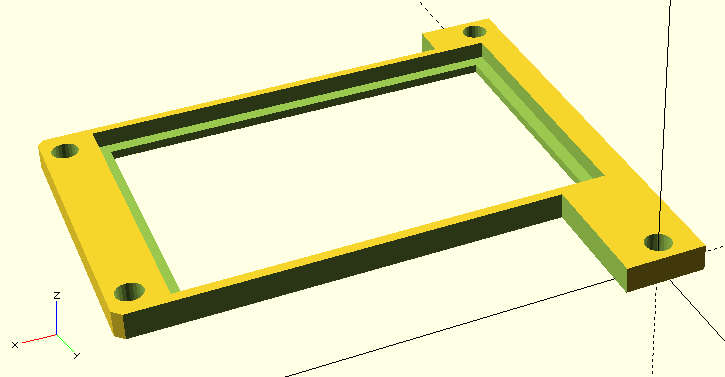
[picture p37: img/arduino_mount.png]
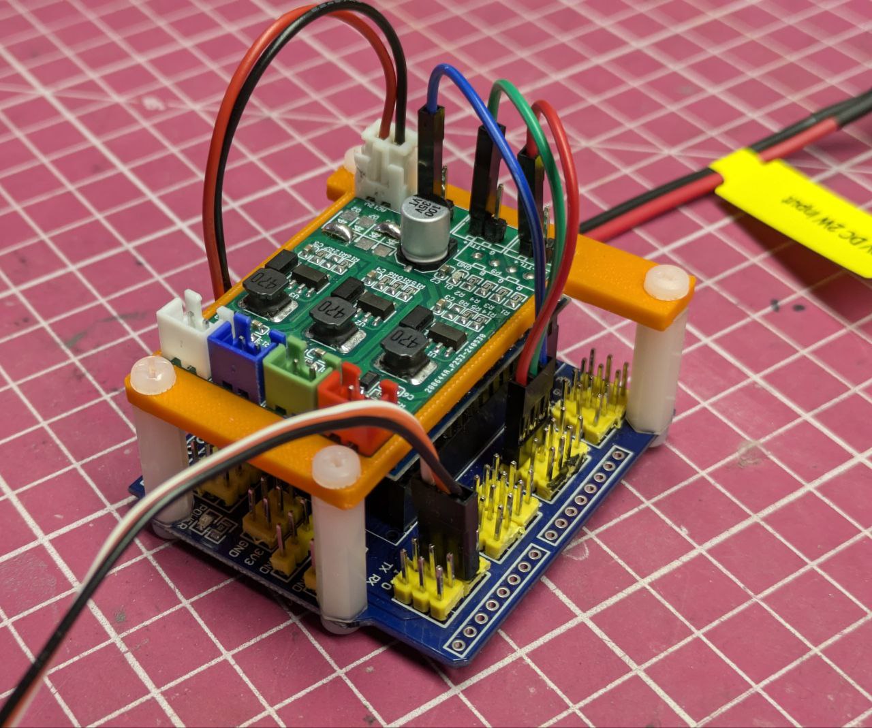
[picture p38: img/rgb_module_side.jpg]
 |  

For arduino operating details see [Step-by-step to controlling multiple light sources with an Arduino](https://github.com/nimwegenLab/MiM_NikonTi/blob/master/Docs/NikonTi_hardware_triggering.m).

---

# Software
All control is provided with [Micro-Manager](https://micro-manager.org/) and [pymmcore-plus](https://pymmcore-plus.github.io/pymmcore-plus/) library with [napari-micromanager](https://pymmcore-plus.github.io/napari-micromanager/) GUI.

__Configuration__
|Component | Desctiption | Micro-manager adapter| Note |
|- | - | - | - |
|Camera | FLIR Grasshopper3 USB3 | [Point Grey Research](https://micro-manager.org/Point_Grey_Research)| |
|Stage | Servo stage | [CustomArduino](https://micro-manager.org/CustomArduino) (MarzhauserLStep Z-stage)| Set AnswerTimeout to 5000.000 |
|Lasers | RGB laser control wtih TTL | [Arduino](https://micro-manager.org/Arduino)| Change MM Ardu version in sketch to 2 |

## Useful links

- [Grasshopper3 USB 3.1 manual, PDF](https://www.physics.utoronto.ca/apl/fvf/GS3-U3-Technical-Reference.pdf)
- [Step-by-step to controlling multiple light sources with an Arduino for sequenceable MDA by Guillaume Witz & Thomas Julou](https://github.com/nimwegenLab/MiM_NikonTi/blob/master/Docs/NikonTi_hardware_triggering.md)

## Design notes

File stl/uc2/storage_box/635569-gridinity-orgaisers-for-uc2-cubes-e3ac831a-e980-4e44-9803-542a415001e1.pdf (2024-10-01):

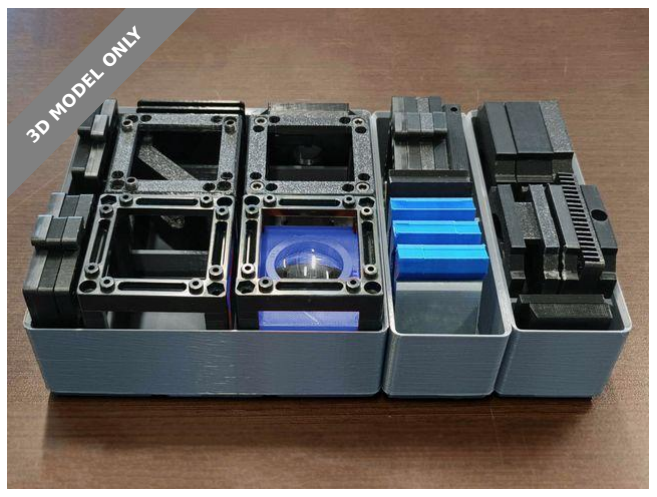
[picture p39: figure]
3D MODEL ONLY

# Summary

Organizing system applied for the UC2 optics cubes, using Gridfinity. It

Includes the grid for an IKEA Helmer furniture.

Hobby & Makers (https://printables.com/model?categoryId=48) | > | Organizers (https://printables.com/model?categoryId=50)
Tags: organizer | ikea | holder | cube | lab | laboratory
opensource | labs | drawer | microscope | | drawerorganizer
helmer | microscopy | optics | ikeahelmer | gridfinity

The first organizers for the UC2 optics cubes, using the gridfinity format.

These can help to keep the laboratory's components safely organised

using the minimum space.

This was printed using PLA, with a 15% infill.

If you want to make any changes, see our CAD design Onshape document. (https://cad.onshape.com/documents/7fc82565fadec94e13904489/w/ad2f5ad420cacab065c58a81/e/cb1aaa225b406741a5ace283?renderMode=0&uiState=654a9b9027c2b61dcfe9d819)

It includes a grid that is designed to fit perfectly inside the "IKEA Helmer" (https://www.ikea.com/cl/es/p/helmer-cajonera-negro-20341970/#content)

drawers.

To know more about the UC2 project, see the UC2 Optics cubes (https://www.printables.com/model/514706-uc2-optics-cubes) advances

and the original GitHub repository. (https://github.com/openUC2/UC2-GIT.) This item was designed by LIBRE hub

Design Technology Fellow Matías Hurtado.

LIBRE hub (https://printables.com/@WenzelLab)

# Gridinity orgaisers for UC2 cubes

### VIEW IN BROWSER (https://printables.com/model/635569-gridinity-orgaisers-for-uc2-cubes)

updated 1. 12. 2023 | published 1. 12. 2023

# Model files

# License

This work is licensed under a

Creative Commons (4.0 International License)

Attribution (http://creativecommons.org/licenses/by/4.0/)

### ✖ | Sharing without ATTRIBUTION

✔ | Remix Culture allowed
✔ | Commercial Use

uc2-cubes-complements.stl

uc2-complements-puzzles-and-mirrors.stl

uc2-complements-inner-pieces.stl

ikea-grid-1.stl

ikea-grid-2.stl

ikea-grid-3.stl

✔ | Free Cultural Works
✔ | Meets Open Definition

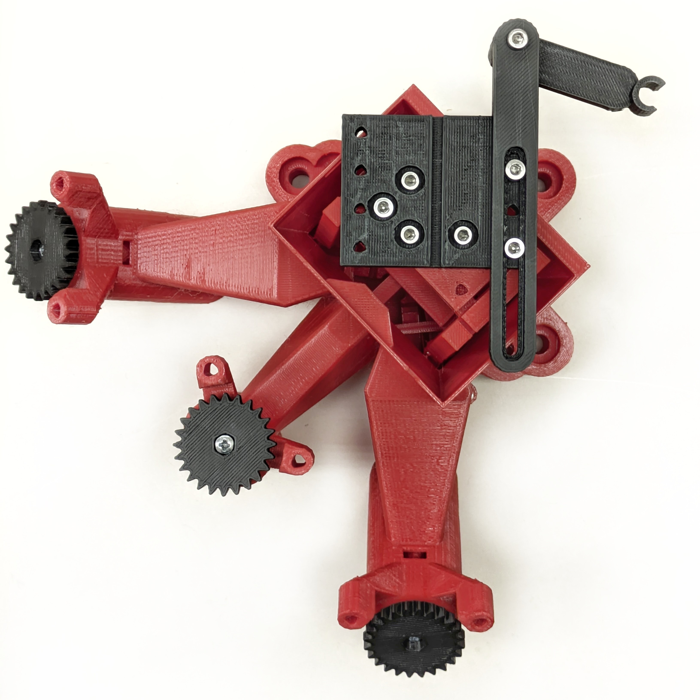
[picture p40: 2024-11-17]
img/of_bs_top.jpg

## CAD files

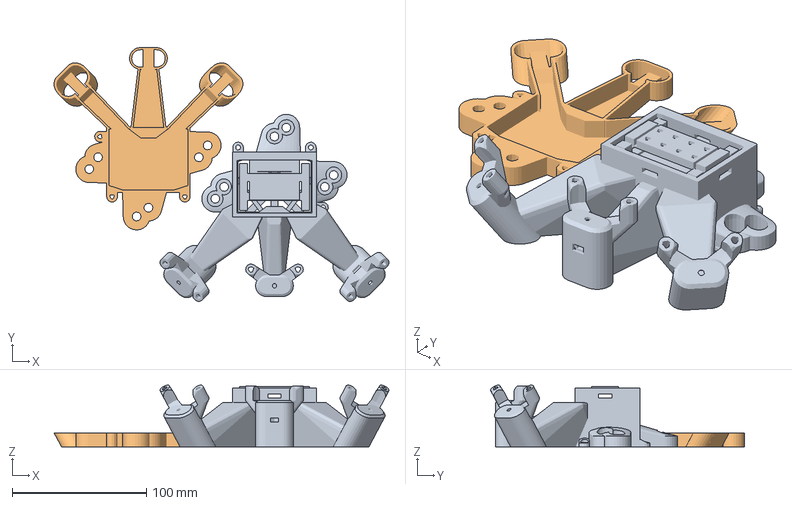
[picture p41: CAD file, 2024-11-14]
scad/OpenFlexure/K1/main_body_00.3mf
249.4 x 188.9 x 46.1 mm
main_body.stl
base.stl

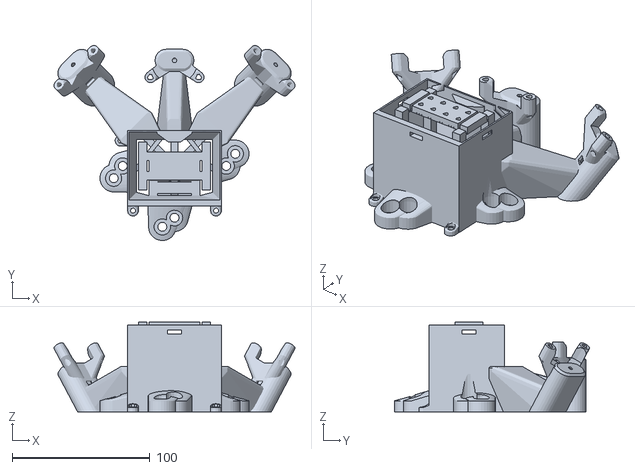
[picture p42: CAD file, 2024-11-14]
scad/OpenFlexure/builds/main_body.stl
174.8 x 141.4 x 65.0

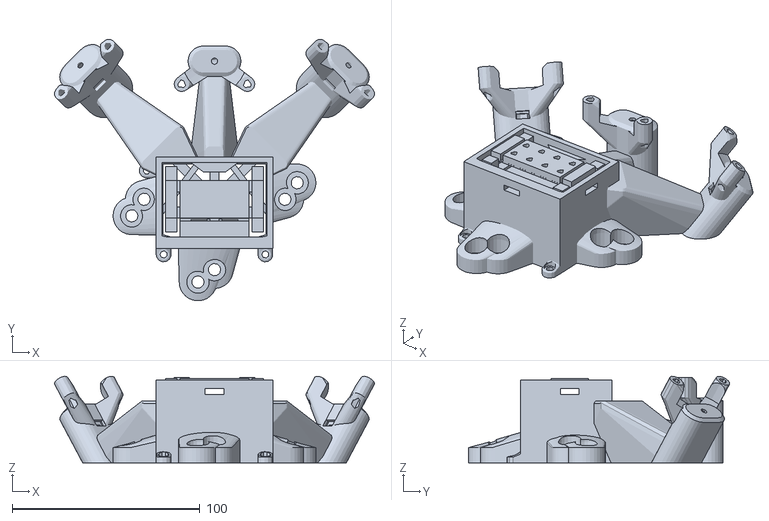
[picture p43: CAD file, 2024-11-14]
scad/OpenFlexure/builds_native/main_body.stl
170.5 x 139.3 x 46.1

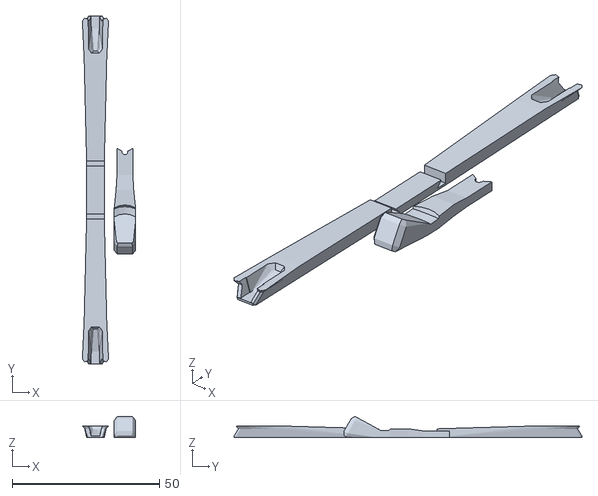
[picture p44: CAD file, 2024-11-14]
scad/OpenFlexure/builds_native/actuator_assembly_tools.stl
18.1 x 118.2 x 7.23

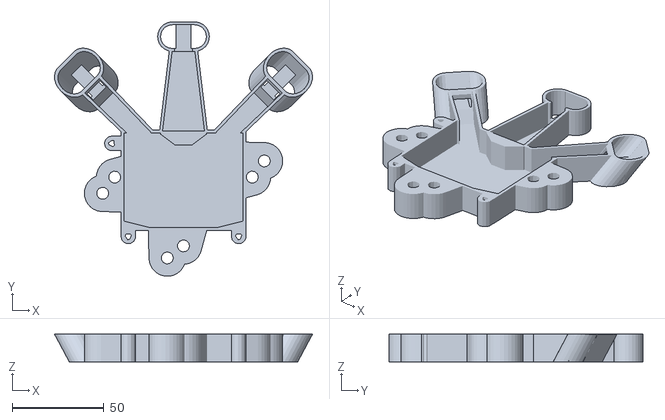
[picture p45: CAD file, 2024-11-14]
scad/OpenFlexure/builds/base.stl
140.6 x 138.7 x 15.0

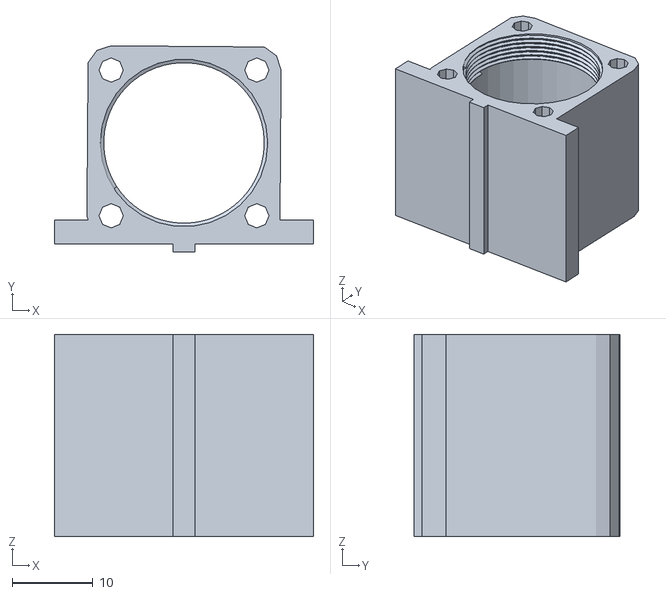
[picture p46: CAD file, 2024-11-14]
scad/OpenFlexure/builds_native/accessories/rms_to_top_plate.stl
32.0 x 25.5 x 25.0

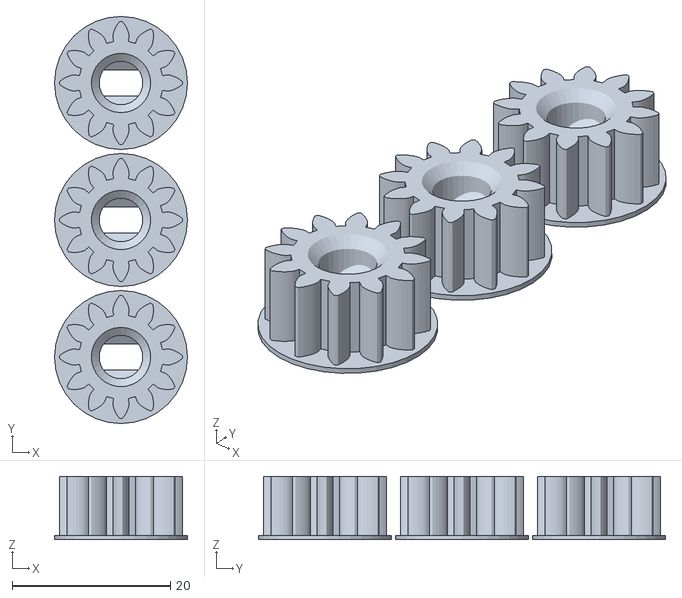
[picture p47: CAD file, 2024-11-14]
scad/OpenFlexure/builds_native/small_gears.stl
16.8 x 51.5 x 8.00

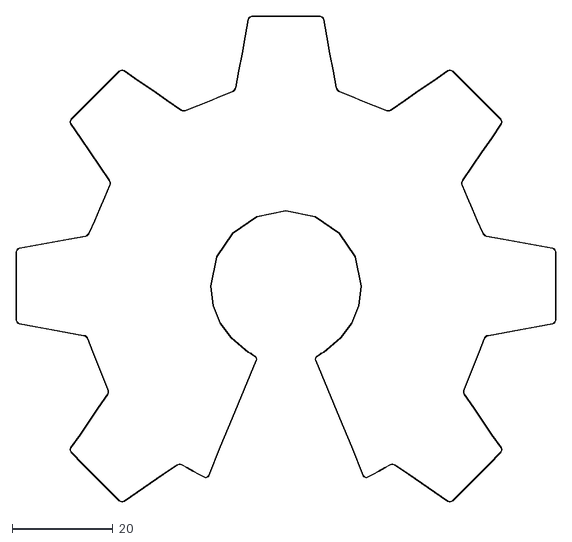
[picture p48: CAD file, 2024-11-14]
scad/OpenFlexure/openscad_native/oshw_gear.dxf
107.1 x 96.4

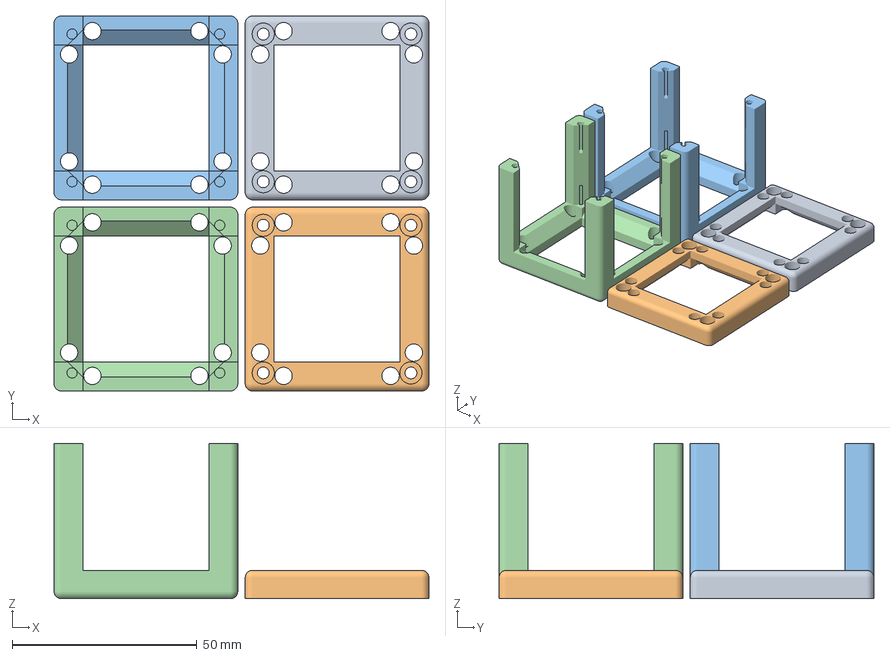
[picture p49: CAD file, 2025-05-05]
stl/00_UC2_v3_cube.3mf
101.6 x 101.6 x 42.1 mm
UC2_v3_10_Lid_1x1_v3.stl x 2
UC2_v3_10_Cube_1x1_v3.stl x 2

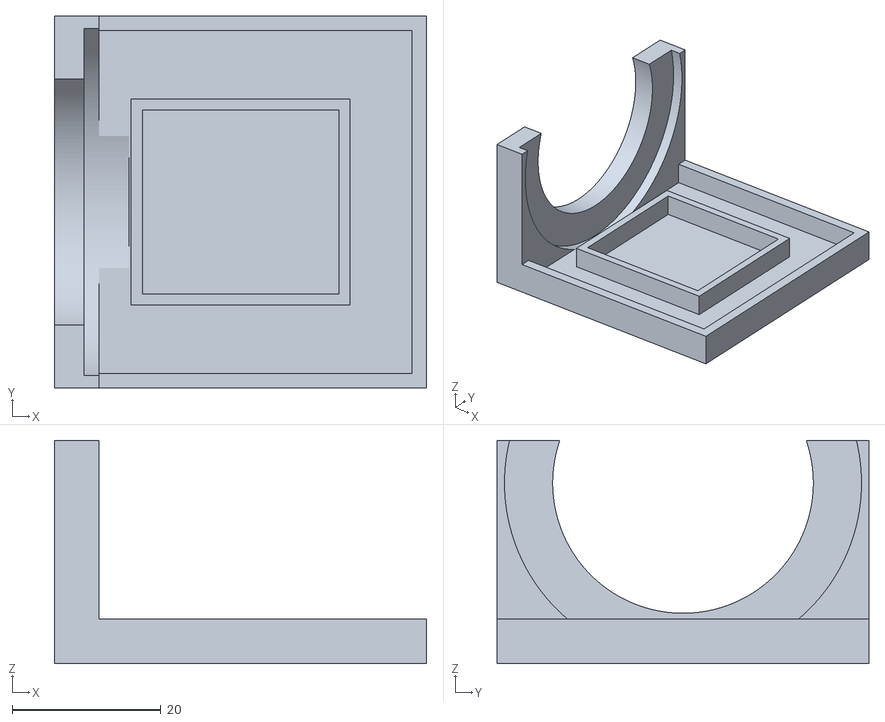
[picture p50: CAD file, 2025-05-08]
stl/original/30_chamber_with_led_v0.stl
50.0 x 50.0 x 30.0

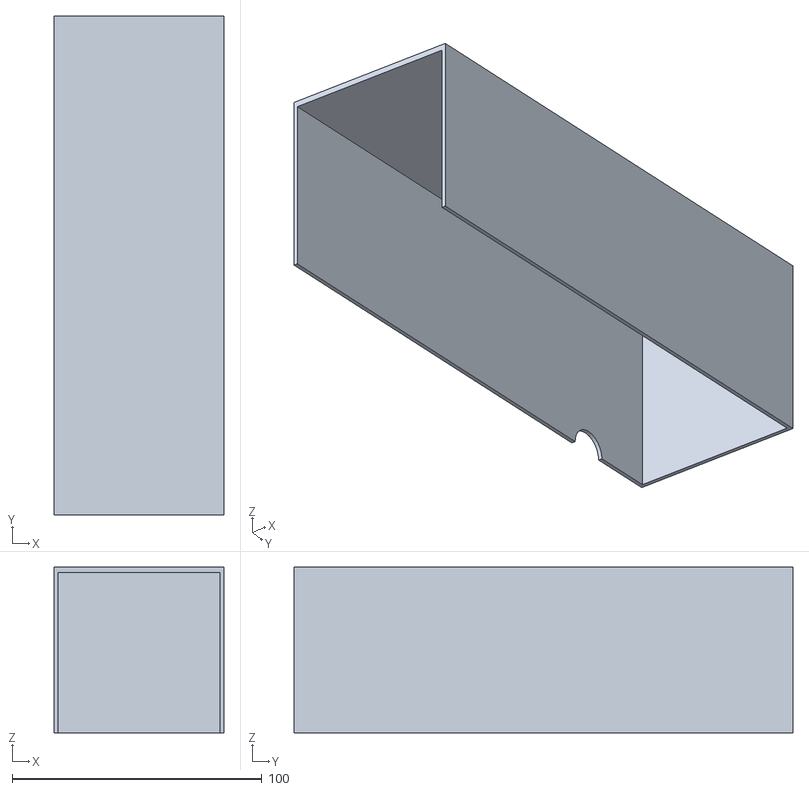
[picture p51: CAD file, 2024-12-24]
stl/original/cubes_enclosure/30_laser_enclosure_v0.stl
68.0 x 200.0 x 66.5

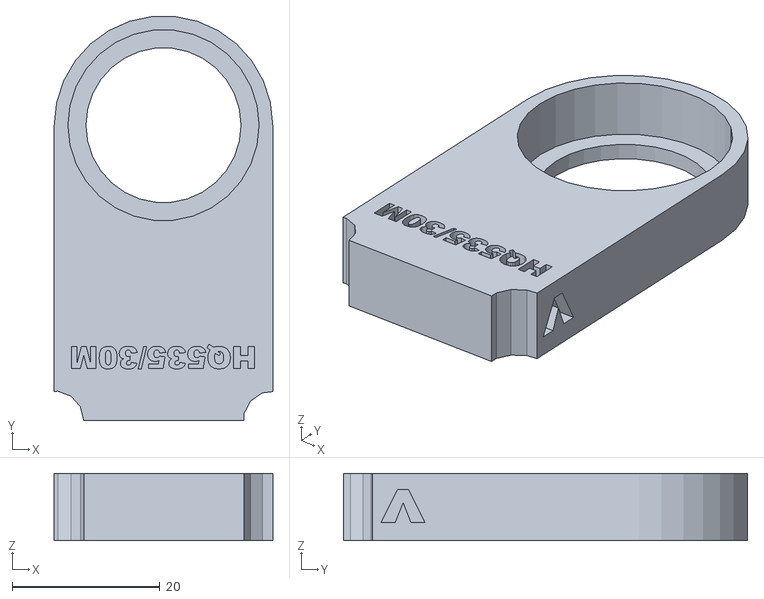
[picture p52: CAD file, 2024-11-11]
stl/original/filter_slider/20_insert_filter_slider_v1_slider_hq535.stl
29.6 x 54.7 x 9.10

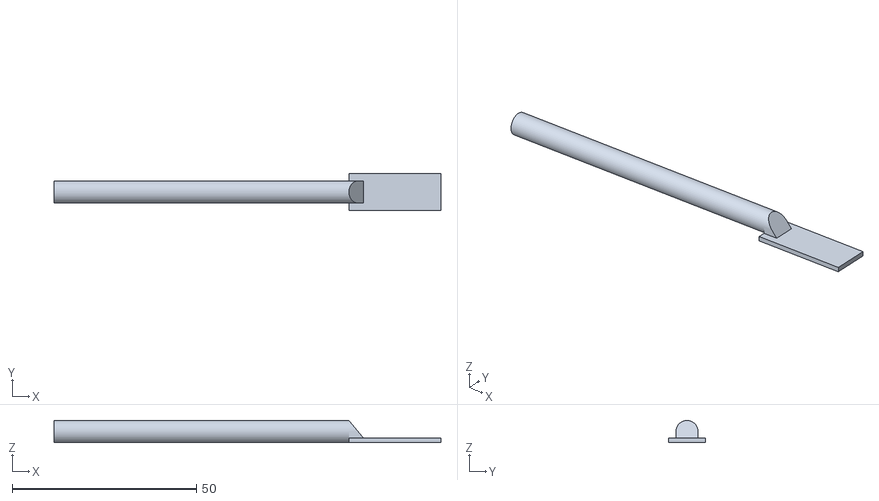
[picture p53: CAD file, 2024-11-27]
stl/original/of_block_stage/00_of_sample_plate_v0.stl
105.0 x 10.0 x 5.99

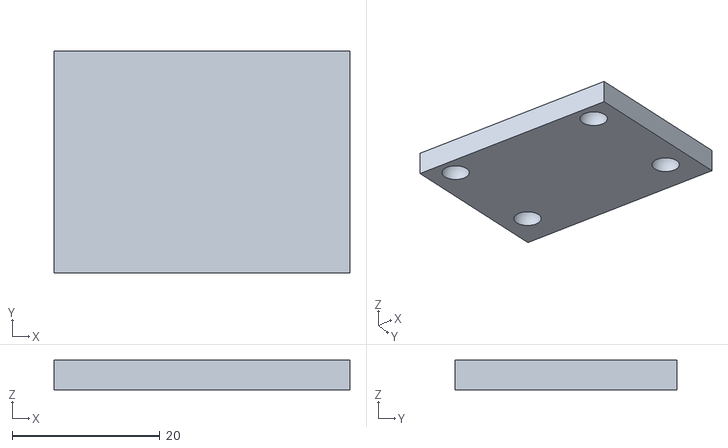
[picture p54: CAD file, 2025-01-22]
stl/uc2/20_Cube_Insert_Kinematic_Mirrormount_45_Plate_v3.stl
40.0 x 30.0 x 4.00

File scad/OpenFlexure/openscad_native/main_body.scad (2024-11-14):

use <utilities.scad>;
use <compact_nut_seat.scad>;
use <fibre_stage_three_legs.scad>;
include <parameters.scad>;

module exterior_brim(r=4, h=0.2){
    // Add a "brim" around the outside of an object *only*, preserving holes in the object
    children();
    
    if(r>0) linear_extrude(h) difference(){
        offset(r) projection(cut=true) translate([0,0,-d]) children();
       
        offset(-r) offset(r) projection(cut=true) translate([0,0,-d]) children();
    }
}
module z_base(){
    // Trapezoid that forms the base of the Z stage
    t = xy_bottom_travel;
    w = z_stage_base_w;
    hull(){
        translate([-pw,-pw-t,0]) cube([2*pw,d,d]); // inner edge
        translate([-w/2, -stage[1]/2-t, 0]) cube([w, d, d]);
        translate([-w/2, z_stage_base_y, 0]) cube([w, d, d]);
    }
}

module z_stage(){
    // This is the part that moves in Z only, connected to the middle
    // "shelf" of the XY table
    // The triangular base of this part must fit between the 
    // pushsticks for the XY motion, which constrains the tip position
    // and also means we must bring the sides out at 45 degrees.
    difference(){
        sequential_hull(){
            z_base();
            translate([0,0,stage[2]]) z_base();
            translate([0,0,shelf_z1 + stage[2]/2]) cube(stage,center=true);
        }
        
        // clearance for Z pushstick (see below)
        translate([-pw/2-1.5, -99, z_pushstick_z - 2 - z_travel]){
            cube([pw+3, 999, pushstick[2]+3.5+2*z_travel]);
        }
    }
    // Join the stage to the anchor with some flexures at the bottom
    reflect([1,0,0]) translate([-z_stage_base_w/2,z_anchor_bottom_y-d,0])
        cube([zflex[0], z_lever + zflex[1]+2*d, zflex[2]]);
    translate([-z_stage_base_w/2,z_anchor_bottom_y+zflex[1],0])
        cube([z_stage_base_w, z_lever - zflex[1], pushstick[2]]);
    // And more flexures at the top
    reflect([1,0,0]) translate([-stage[0]/2,-stage[1]/2,shelf_z1]) mirror([0,1,0]){
        translate([0,-d,0]) cube([zflex[0], z_lever + zflex[1]+2*d, zflex[2]]);
        translate([0,zflex[1],dz]) cube([stage[0]/2+d,z_lever - zflex[1], stage[2]-dz]);
    }
    // The actuating "pushstick" attaches to this lever
    hull(){
        translate([-pw/2, z_stage_base_y - z_lever, 0]) cube([pw, z_lever - zflex[1], stage[2]]);
        translate([-pw/2, z_stage_base_y - 3 - zflex[1], 0]) cube([pw, 3, shelf_z1 - 3]);
    }
    // This is the actuating "pushstick"
    translate([-pw/2, z_stage_base_y, z_pushstick_z]){
        l = z_actuator_pivot_y - z_stage_base_y;
        cube([pw, l, pushstick[2]]);
        translate([0,-zflex[1]*2,0]) cube([pw, l + 4*zflex[1], zflex[2]]);
    }
}

// Overall structure
module main_body(){
    difference(){
        xy_table();
        
        // cutouts for pushsticks
        each_pushstick() hull() {
            h=stage[2]*2+z_travel*2;
            translate([0,2*d,0]) cube([pw, d, h], center=true);
            translate([0,0.5,0]) cube([pw+1.5, d, h], center=true);
            translate([0, pushstick[1], 0]) cube([pw+1+2*xy_bottom_travel*sqrt(2), d, h], center=true);
            translate([0, pushstick[1], 0]) cube([d, d, h + pw+1+2*xy_bottom_travel*sqrt(2)], center=true);
            translate([99, 98, 0]) cube([d, d, h + pw+1+2*xy_bottom_travel*sqrt(2)], center=true); //cut out between the pushsticks
        }
        
        // cutout for Z stage
        hull(){
            h=stage[2]*2+z_travel*2;
            w = stage[0] - 2*zflex[1];
            translate([0, -pw, 0]) cube([2*pw,d,h],center=true);
            translate([0, -stage[1]/2, 0]) cube([w,2*d,h],center=true);
        }
        
        // mounting holes on top
        repeat([10,0,0],4,center=true)
            repeat([0,10,0],2,center=true)
            translate([0,0,shelf_z2 + 1.5]) trylinder_selftap(3,h=999);
            // NB the z position must clear the bottom of the stage
            // (which is 1mm above shelf_z2) or we get errors on the
            // bridge.
    }
    // XY pushsticks and actuators
    each_pushstick(){
        pushstick();
        translate([0,pushstick[1] - zflex[1],0]) tilted_actuator(shelf_z1, xy_actuator_pivot_w, xy_lever * xy_reduction, base_w = pw);
    }
    
    // Z stage (the part that moves only in Z) and actuator
    z_stage();
    translate([0,z_actuator_pivot_y,0]){
        untilted_actuator(z_pushstick_z, z_actuator_pivot_w, z_lever * z_reduction);
    }
    //reinforcement through the void in the centre
    reflect([1,0,0]) translate([0,0,pushstick[2] + 4 + z_travel]) hull(){
        translate([pw/2+3, z_actuator_pivot_y - wall_t, 0]) cube([4,d,4]);
        translate([stage[0]/2 + zflex[0] + zflex[1] + xy_bottom_travel, -stage[1]/2,0]) cube([0.5,4,4]);
    }
    
    // Casing (also provides a lot of the structural integrity)
    casing();
    // if(fixed_platform) fixed_platform(); <<<<<<<<<<<<<<<<<<
        
    
}//*/
brim_r=0;
exterior_brim(r=brim_r) main_body();

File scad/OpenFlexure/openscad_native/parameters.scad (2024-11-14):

/*
  Useful settings/parameters for the OpenFlexure fibre stage
*/
version_numstring = "0.2.1";
stage = [37,20,5]; // dimensions of stage part
beam_height = 100; // 75 <<<<<< height of beam above the table
stage_to_beam_height = 12.5;
stage_height = beam_height - stage_to_beam_height; //bottom of base to top surface of the stage 
 // NB platform_z sets the distance from bottom of the body to top of the stage
 // stage_height determines the thickness of the base.
brim_r = 0;

// Range of travel is lever length * flex_a
xy_lever = 20;  // 10 <<<<<<<<<<<<<<<<<<<<<
z_lever = 20;   // 10 <<<<<<<<<<<<<<<<<<<<<

// Mechanical reduction settings
xy_stage_reduction = 30/xy_lever; //ratio of sample motion to lower shelf motion
xy_reduction = 50/xy_lever; //mechanical reduction from screw to sample
z_reduction = 50/z_lever; //mechanical reduction for Z

// Motor lugs
motor_lugs = true;

// fixed platform for fibre launch
//fixed_platform = false; // this is overwritten later on with the dimensions anyway.

// Mounting holes
breadboard_lugs="diagonal"; //sets the hole pattern for bolting it down.  See the options below.

// Flexure dimensions - good for PLA and ~0.5mm nozzle
zflex = [6, 1.5, 0.75]; //dimensions of flexure
xflex = [5,5.5,5]; //default bounding box of x flexure
xflex_t = 1; //thickness of bendy bit in x
flex_a = 0.1; //angle through which flexures are bent, radians, 0.1 <<<<<
dz = 0.5; //thickness before a bridge is printable-on

xy_travel = xy_lever * flex_a; //max. travel in X or Y
xy_bottom_travel = xy_travel * xy_stage_reduction; //travel of bottom of XY stage
xy_actuator_pivot_w = 25; //width of the hinge for the actuating lever
actuator_h = 26; //height of actuator columns (~screw length)

pushstick = [5,38,5]; //cross-section of XY "push stick"
pw = pushstick[0]; //because this is used in a lot of places...

wall_t = 1.6;
d=0.05;

// Height of the bridging "shelves" in the XY axis "table" structure
shelf_z1 = xy_lever * xy_stage_reduction;
shelf_z2 = shelf_z1 + xy_lever;

// Z axis geometry
z_travel = z_lever * flex_a; //max. travel in Z
z_stage_base_y = -stage[1]/2-xy_bottom_travel; //position of the flexure edge of the Z stage
z_stage_base_w = stage[0] + 2*zflex[1] - 2*xy_bottom_travel - 2; //width of the flexure edge of the Z stage
z_anchor_bottom_y = z_stage_base_y - z_lever - zflex[1]; // lower Z stage end of the fixed base
z_actuator_pivot_y = stage[1]/2 + zflex[1] + zflex[0] + xy_bottom_travel + wall_t;
z_actuator_pivot_w = 20; //width of the hinge for the Z actuator lever
z_pushstick_z = shelf_z1 - pw - 2.5; // height of the Z pushstick

// Mounting stuff
// By default, place 3 mounting holes to align the centre of the stage with a hole.
// setting beam_between_holes adds another set of holes, putting the beam halfway between
bolt_spacing = 25; // change to 25.4 for imperial tables
mounting_bolts_alongholes = [[-1,0,0],[0,-1,0],[1,0,0]]*1.5*bolt_spacing; //beam aligned with holes
mounting_bolts_betweenholes = [[-1.25,-0.25,0],[1.25,0.25,0],[-0.25,-1.25,0]]*1.41*bolt_spacing;
mounting_bolts_atsides = [[-1.5,0,0],[1.5,0,0],[-1.5,-1,0],[1.5,-1,0]] * bolt_spacing;
mounting_bolts_diagonal = concat(mounting_bolts_alongholes, 
                                 mounting_bolts_betweenholes);
// I hope you'll excuse the stacked ternaries, this is an unpleasant necessity :(
mounting_bolts = breadboard_lugs=="atsides"?mounting_bolts_sides:
                 breadboard_lugs=="diagonal"?mounting_bolts_diagonal:
                 breadboard_lugs=="alongholes"?mounting_bolts_alongholes:
                 breadboard_lugs=="betweenholes"?mounting_bolts_betweenholes:
                 /*breadboard_lugs=="none"?*/[];
            
platform_z = shelf_z2 + stage[2] + 22.5; // 7 <<<<<<< The platform is a fixed height above the moving stage
fixed_platform_standoff = 10;
fixed_platform = [50,40,4];
platform_gap = xy_travel + 1;

//term for calculating casing size
casing_size_s = xy_bottom_travel + zflex[1] + zflex[0] + 0.5 + wall_t;
//casing size
casing_size = stage + [2*casing_size_s,casing_size_s + (-z_anchor_bottom_y-stage[1]/2) + wall_t,shelf_z2];
casing_top = shelf_z2 + stage[2] - z_travel; // top of the wall
max_actuator_travel = max(xy_travel*xy_reduction, z_travel*z_reduction); // maximum distance the actuators protrude below the stage
base_height = stage_height - platform_z; // the base takes up any height not use by the body.
if(base_height < max_actuator_travel + 4) echo("WARNING: stage_height is too low, base will not compile properly!");

//foot_height is required for the actuator assembly tools
foot_height = 20;

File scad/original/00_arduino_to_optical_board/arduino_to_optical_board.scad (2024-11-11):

// thickness of the PCB
board_height = 5;

// solid_holes - specifies if mounting holes should be added to or subtracted from the model
// combined_headers - specifies if space should be left between adjacent female headers, or if they should be rendered as a single header
// extend_ports - extends the USB and power ports by a centimeter, so that holes are more easily made when a model is used as a negative

module Board()
{
	color([0, 0.6, 0.8])
	linear_extrude(height = board_height, convexity = 10, twist = 0)
	{
		polygon( points = [ [-4.115, 2.545],
						[49.4, 2.545],
						[50.925, 1.021],
						[50.925, -10.409],
						[53.465, -12.949],
						[53.465, -45.715],
						[50.925, -48.255],
						[50.925, -50.795],
						[-4.115, -50.795] ],
				paths = [[0, 1, 2, 3, 4, 5, 6, 7, 8]],
				convexity = 10);
	}
}

module ArduinoMount() {
    difference() {
        scale([1.2,1.2,2])
            Board();
        translate([7,-7,0])
        scale([0.9,0.9,2])
            Board();
        translate([5,-5,8])
            Board();
        
        translate([52,-3.5,2])
            cylinder(d = 10.25,h = 20);
        translate([52,-3.5,0])
            cylinder(d = 6,h = 20);
        translate([2,-3.5,2])
            cylinder(d = 10.25,h = 20);
        translate([2,-3.5,0])
            cylinder(d = 6,h = 20);
        
        translate([-10,-50.5,4])
            cube([40,40,10]);
        translate([5.5,-70,4])
            cube([45,40,10]);
        translate([41,-50.5,4])
            cube([45,32,10]);
    }
}

ArduinoMount();

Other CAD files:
stl/uc2/storage_box/uc2-complements-puzzles-and-mirrors.stl
scad/OpenFlexure/builds_native/accessories/LED_to_top_plate.stl
scad/OpenFlexure/K1/moving_platform_00.3mf
stl/original/30_tube_enclosure_OUT_v0.stl
scad/original/30_chamber_with_LED/20_insert_for_chamber_with_led_controller_v0.scad
scad/OpenFlexure/builds_native/accessories/CPS532_to_top_plate.stl
scad/OpenFlexure/builds_native/accessories/vertical_sample_clips.stl
scad/OpenFlexure/builds_native/base.stl
scad/OpenFlexure/builds_native/gears.stl
scad/OpenFlexure/builds_native/moving_platform.stl
scad/OpenFlexure/openscad_native/accessories/CPS532_to_top_plate.scad
scad/OpenFlexure/openscad_native/accessories/LED_to_top_plate.scad
scad/OpenFlexure/openscad_native/accessories/cylinder_clamp.scad
scad/OpenFlexure/openscad_native/accessories/microscope_module.scad
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

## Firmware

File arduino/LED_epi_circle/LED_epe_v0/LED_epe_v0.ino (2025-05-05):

#include <FastLED.h>
#include <Encoder.h>

#define LED_PIN     6      // Пін для підключення Data In гірлянди
#define NUM_LEDS    16     // Кількість LED в гірлянді (змініть на свою)
#define BRIGHTNESS  32    // Яскравість за замовчуванням (0-255)
#define MAX_BRIGHTNESS 64 // Максимальна яскравість
#define LED_TYPE    WS2812B  // Тип LED
#define COLOR_ORDER GRB     // Порядок кольорів

// Піни енкодера
#define ENCODER_PIN_A 2
#define ENCODER_PIN_B 3
#define ENCODER_BUTTON 4   // Пін для кнопки енкодера

// Режими роботи
#define MODE_MOVE     0    // Режим руху сегмента
#define MODE_BRIGHTNESS 1  // Режим регулювання яскравості
#define MODE_LENGTH   2    // Режим регулювання довжини сегмента

CRGB leds[NUM_LEDS];
Encoder myEncoder(ENCODER_PIN_A, ENCODER_PIN_B);

// Variables for tracking
long oldPosition = 0;      // Previous encoder position
int segmentLength = 8;     // Length of illuminated segment
int currentPosition = 0;   // Current position of the first LED in segment
int currentMode = MODE_MOVE; // Current operating mode
int currentBrightness = BRIGHTNESS; // Current brightness level
bool ledsOn = true;        // Flag for LEDs on/off state

// Colors for different modes
CRGB moveColor = CRGB::White;      // Color when in movement mode
CRGB brightnessColor = CRGB::White; // Color when in brightness mode
CRGB lengthColor = CRGB::Red;     // Color when in length mode

// Button handling variables
int buttonState = HIGH;     // Current button state
int lastButtonState = HIGH; // Previous button state
unsigned long lastDebounceTime = 0;  // Last debounce time
unsigned long debounceDelay = 50;    // Debounce time in ms

// Double-click detection
unsigned long lastClickTime = 0;
unsigned long doubleClickDelay = 300; // Max time between clicks to count as double-click
bool awaitingDoubleClick = false;

// Long press detection
unsigned long buttonPressStart = 0;
bool longPressHandled = false;
unsigned long longPressDuration = 2000; // 2 seconds for long press

void setup() {
  // Initialize FastLED
  FastLED.addLeds<LED_TYPE, LED_PIN, COLOR_ORDER>(leds, NUM_LEDS)
    .setCorrection(TypicalLEDStrip);
  FastLED.setBrightness(currentBrightness);
  
  // Set up button with internal pull-up resistor
  pinMode(ENCODER_BUTTON, INPUT_PULLUP);
  
  // Initialize serial for debugging
  Serial.begin(9600);
  Serial.println("Starting LED ring control with encoder");
  Serial.println("Default mode: MOVE SEGMENT");
  Serial.println("Single click: Toggle brightness adjustment");
  Serial.println("Double click: Toggle segment length adjustment");
  Serial.println("Long press (2s): Turn LEDs on/off");
  
  // Initial LED update
  updateLEDs();
}

void loop() {
  // Only process encoder if LEDs are on
  if (ledsOn) {
    // Read encoder position (divide by 4 to reduce sensitivity)
    long newPosition = myEncoder.read() / 4;
    
    // Check if position has changed
    if (newPosition != oldPosition) {
      switch (currentMode) {
        case MODE_MOVE:
          // MOVE SEGMENT MODE
          if (newPosition > oldPosition) {
            // Clockwise rotation - move segment forward
            currentPosition = (currentPosition + 1) % NUM_LEDS;
          } else {
            // Counter-clockwise rotation - move segment backward
            currentPosition = (currentPosition - 1 + NUM_LEDS) % NUM_LEDS;
          }
          Serial.print("Position: ");
          Serial.println(currentPosition);
          break;
          
        case MODE_BRIGHTNESS:
          // BRIGHTNESS ADJUSTMENT MODE
          if (newPosition > oldPosition) {
            // Increase brightness (max is MAX_BRIGHTNESS)
            currentBrightness = min(currentBrightness + 5, MAX_BRIGHTNESS);
          } else {
            // Decrease brightness (min is 5)
            currentBrightness = max(currentBrightness - 5, 5);
          }
          FastLED.setBrightness(currentBrightness);
          Serial.print("Brightness: ");
          Serial.println(currentBrightness);
          break;
          
        case MODE_LENGTH:
          // SEGMENT LENGTH MODE
          if (newPosition > oldPosition) {
            // Increase segment length (max is NUM_LEDS)
            segmentLength = min(segmentLength + 1, NUM_LEDS);
          } else {
            // Decrease segment length (min is 1)
            segmentLength = max(segmentLength - 1, 1);
          }
          Serial.print("Segment Length: ");
          Serial.println(segmentLength);
          break;
      }
      
      // Update old position
      oldPosition = newPosition;
      
      // Update LEDs
      updateLEDs();
    }
  }
  
  // Button handling for mode switching and power toggle
  int reading = digitalRead(ENCODER_BUTTON);
  
  if (reading != lastButtonState) {
    lastDebounceTime = millis();
  }
  
  if ((millis() - lastDebounceTime) > debounceDelay) {
    if (reading != buttonState) {
      buttonState = reading;
      
      // Button press detected (LOW when using INPUT_PULLUP)
      if (buttonState == LOW) {
        // Button pressed - start timing for long press
        buttonPressStart = millis();
        longPressHandled = false;
      } else {
        // Button released - check if it was a long press
        unsigned long pressDuration = millis() - buttonPressStart;
        
        if (pressDuration >= longPressDuration && !longPressHandled) {
          // Long press detected - toggle LEDs on/off
          ledsOn = !ledsOn;
          Serial.print("LEDs toggled: ");
          Serial.println(ledsOn ? "ON" : "OFF");
          updateLEDs();
          longPressHandled = true;
        } else if (pressDuration < longPressDuration && !longPressHandled) {
          // Short press - handle regular button press
          handleButtonPress();
        }
      }
    }
  }
  
  // Check if we're awaiting a double click and time is up
  if (awaitingDoubleClick && (millis() - lastClickTime > doubleClickDelay)) {
    awaitingDoubleClick = false;
    
    // We had a single click (not a double), so switch to brightness mode
    if (currentMode != MODE_BRIGHTNESS) {
      currentMode = MODE_BRIGHTNESS;
      Serial.println("Mode changed: BRIGHTNESS ADJUSTMENT");
      updateLEDs();
    } else {
      // If already in brightness mode, go back to move mode
      currentMode = MODE_MOVE;
      Serial.println("Mode changed: MOVE SEGMENT");
      updateLEDs();
    }
  }
  
  lastButtonState = reading;
}

void handleButtonPress() {
  unsigned long currentTime = millis();
  
  // Check if this could be a double click
  if (awaitingDoubleClick) {
    // This is a double click!
    awaitingDoubleClick = false;
    
    // Set to length adjustment mode
    currentMode = MODE_LENGTH;
    Serial.println("Mode changed: SEGMENT LENGTH ADJUSTMENT");
    updateLEDs();
  } else {
    // This might be the first click of a double click
    lastClickTime = currentTime;
    awaitingDoubleClick = true;
    
    // If in length mode, single click returns to move mode
    if (currentMode == MODE_LENGTH) {
      currentMode = MODE_MOVE;
      awaitingDoubleClick = false; // Cancel double-click detection
      Serial.println("Mode changed: MOVE SEGMENT");
      updateLEDs();
    }
  }
}

void updateLEDs() {
  // Clear all LEDs
  fill_solid(leds, NUM_LEDS, CRGB::Black);
  
  // If LEDs are turned off, just show all black
  if (!ledsOn) {
    FastLED.show();
    return;
  }
  
  // Select color based on current mode
  CRGB currentColor;
  int displayBrightness = currentBrightness;
  
  switch (currentMode) {
    case MODE_MOVE:
      currentColor = moveColor;
      break;
    case MODE_BRIGHTNESS:
      currentColor = brightnessColor;
      break;
    case MODE_LENGTH:
      currentColor = lengthColor;
      displayBrightness = 16; // Fixed low brightness in length mode
      break;
  }
  
  // Illuminate the segment with ring wraparound
  for (int i = 0; i < segmentLength; i++) {
    // Calculate position with ring wraparound
    int pos = (currentPosition + i) % NUM_LEDS;
    leds[pos] = currentColor;  // Set segment color based on mode
  }
  
  // In brightness mode, use the current brightness
  // But in length mode, override with fixed low brightness
  if (currentMode == MODE_LENGTH) {
    FastLED.setBrightness(16);
  } else {
    FastLED.setBrightness(currentBrightness);
  }
  
  // Update LEDs
  FastLED.show();
}

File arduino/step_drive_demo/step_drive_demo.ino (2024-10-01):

#include <Encoder.h>
#include <Pushbutton.h>

// joystick set up
const int JxPin = A6;     // joystick X axis pin
const int JyPin = A7;     // joystick Y axis pin
Pushbutton Jbutton(4);    // joystick button pin

int JxPosition = 0;
int JyPosition = 0;

// encoder set up
Encoder zEnc(7,6);       // encoder CLC and DT pins
Pushbutton Ebutton(5);    // encoder button pin

long Eposition  = 0;
long EpositionNew = 0;

// stepper driver set up
const int stepPin = 2;    // A4988 step pin
const int dirPin = 3;     // A4988 dir pin
const int qstepPin = 8;   // A4988 MS2 pin
const int dsleepPin = 9;  // A4988 sleep pin

const int stepDelayL = 400;
const int stepDelayH = 50;

byte qstepState = LOW;
bool isMoove = false;
int stepDelay = stepDelayL;

bool jOrE = false;

void setup() {
  // initialize serial communications at 9600 bps:
  Serial.begin(9600); 

  // initialize j pins 
  pinMode(JxPin, INPUT);
  pinMode(JyPin, INPUT);
  // pinMode(JbuttonPin, INPUT_PULLUP); 

  // initialize stepper pins
  pinMode(stepPin,OUTPUT); 
  pinMode(dirPin,OUTPUT); 
  pinMode(qstepPin,OUTPUT); 
  pinMode(dsleepPin,OUTPUT); 

  digitalWrite(qstepPin, LOW);
  digitalWrite(dsleepPin, LOW);
}

void loop(){
  JxPosition = analogRead(JxPin);
  JyPosition = analogRead(JyPin);

  if (Jbutton.getSingleDebouncedPress() or Ebutton.getSingleDebouncedPress()) {
    if (qstepState == LOW) {
      qstepState = HIGH;
      stepDelay = stepDelayH;
      digitalWrite(qstepPin, qstepState);
    }
    else if (qstepState == HIGH) {
      qstepState = LOW;
      stepDelay = stepDelayL;
      digitalWrite(qstepPin, qstepState);
    }
   }
   
  EpositionNew = zEnc.read(); 
  Serial.println(EpositionNew);

  if (JxPosition > 767 or JyPosition > 767 or JxPosition < 255 or JyPosition < 255 or EpositionNew != Eposition) {
    if (isMoove == false) {
        digitalWrite(dsleepPin, HIGH);
        delay(3);
        isMoove = true;
      } else {
        if (EpositionNew != Eposition) {
          move_enc();
        } else{
          move_joy();
        }
      }
    } else {
      digitalWrite(dsleepPin, LOW);
      isMoove = false;
    }
}

void move_enc() {
  long EpositionDiff = EpositionNew - Eposition;
  Eposition = EpositionNew;
  Serial.println(EpositionDiff);
  if (EpositionDiff > 0) {
    move_clocwise();
  }
  if (EpositionDiff < 0) {
    move_contrclocwise();
  }
}

void move_joy() {
  if (JxPosition > 767 or JyPosition > 767) {
    move_clocwise();
  } 
  if (JxPosition < 255 or JyPosition < 255) {
    move_contrclocwise();
  }
}

void move_clocwise() {
  digitalWrite(dirPin,LOW);
  for(int x = 0; x < 10; x++) {
    digitalWrite(stepPin,HIGH);
    delayMicroseconds(stepDelay);
    digitalWrite(stepPin,LOW);
    delayMicroseconds(stepDelay);
  }
}

void move_contrclocwise(){
  digitalWrite(dirPin,HIGH);
  for(int x = 0; x < 10; x++) {
    digitalWrite(stepPin,HIGH);
    delayMicroseconds(stepDelay);
    digitalWrite(stepPin,LOW);
    delayMicroseconds(stepDelay);
  }
}

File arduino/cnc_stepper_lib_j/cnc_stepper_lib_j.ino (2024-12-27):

// Nano CNC board with stepper lib and joystick control

// #include "A4988.h"
#include <Arduino.h>
#include "BasicStepperDriver.h"
#include "MultiDriver.h"
#include "SyncDriver.h"

// joystick set up
#define X_STICK A7
#define Y_STICK A6
#define J_CLICK 12

#define U_LIM 614
#define D_LIM 414

int xPos = 0;
int yPos = 0;
int bStt = 0;
int bSttLast = 0;
int bPress = 0;

// steppers set up
#define X_STEP 5         // X-axis step pin  X-5, Y-6. Z-7 
#define X_DIR 2          // X-axis dir pin   X-2, Y-3. Z-4 

#define Y_STEP 6         // Y-axis step pin  X-5, Y-6. Z-7 
#define Y_DIR 3          // y-axis dir pin   X-2, Y-3. Z-4 

#define Z_STEP 7         // Z-axis step pin  X-5, Y-6. Z-7 
#define Z_DIR 4          // z-axis dir pin   X-2, Y-3. Z-4 

#define MOTOR_EN 8       // drivers enable pin

#define MOTOR_STEPS 2047  // steps per revolution

BasicStepperDriver stepperX(MOTOR_STEPS, X_DIR, X_STEP);
BasicStepperDriver stepperY(MOTOR_STEPS, Y_DIR, Y_STEP);
BasicStepperDriver stepperZ(MOTOR_STEPS, Z_DIR, Z_STEP);

SyncDriver controller(stepperX, stepperY, stepperZ);

int rotate = 360;


void setup() {
  // initialize serial communications at 9600 bps:
  Serial.begin(9600); 
  
  pinMode(X_STICK, INPUT);
  pinMode(Y_STICK, INPUT);
  pinMode(J_CLICK, INPUT_PULLUP);

  pinMode(MOTOR_EN, OUTPUT);
  digitalWrite(MOTOR_EN, LOW);

  stepperX.begin(15., 1);
  stepperY.begin(15., 1);
  stepperZ.begin(15., 1);

  pinMode(MOTOR_EN, OUTPUT);
  digitalWrite(MOTOR_EN, HIGH);

}


void loop() {
  bState();

  xPos = analogRead(X_STICK);
  yPos = analogRead(Y_STICK);
  
  if (bPress == 0){
    xyMove();
  }
  else if (bPress == 1){
    zMove();
  }

  Serial.print("X: ");
  Serial.print(xPos);
  Serial.print(" | Y: ");
  Serial.print(yPos);
  Serial.print(" | Button: ");
  Serial.println(bPress);
}


void xyMove() {
  if ((xPos > U_LIM) && (yPos > U_LIM)){
    digitalWrite(MOTOR_EN, LOW);
    delayMicroseconds(10);
    controller.rotate(-10, 10, 0);
    }
  else if ((xPos < D_LIM) && (yPos < D_LIM)){
    digitalWrite(MOTOR_EN, LOW);
    delayMicroseconds(10);
    controller.rotate(10, -10, 0);
    }
  else if ((xPos < D_LIM) && (yPos > U_LIM)){
    digitalWrite(MOTOR_EN, LOW);
    delayMicroseconds(10);
    controller.rotate(10, 10, 0);
    }
  else if ((xPos > U_LIM) && (yPos < D_LIM)){
    digitalWrite(MOTOR_EN, LOW);
    delayMicroseconds(10);
    controller.rotate(-10, -10, 0);
    }
  else if (yPos < D_LIM){
    digitalWrite(MOTOR_EN, LOW);
    delayMicroseconds(10);
    controller.rotate(0, -10, 0);
    }
  else if (yPos > U_LIM){
    digitalWrite(MOTOR_EN, LOW);
    delayMicroseconds(10);
    controller.rotate(0, 10, 0);
    }
  else if (xPos < D_LIM){
    digitalWrite(MOTOR_EN, LOW);
    delayMicroseconds(10);
    controller.rotate(10, 0, 0);
    }
  else if (xPos > U_LIM){
    digitalWrite(MOTOR_EN, LOW);
    delayMicroseconds(10);
    controller.rotate(-10, 0, 0);
    }
}


void zMove() {
  if (yPos < D_LIM){
    digitalWrite(MOTOR_EN, LOW);
    delayMicroseconds(10);
    controller.rotate(0, 0, 10);
    }
  else if (yPos > U_LIM){
    digitalWrite(MOTOR_EN, LOW);
    delayMicroseconds(10);
    controller.rotate(0, 0, -10);
    }
}


void bState() {
  int bStt = digitalRead(J_CLICK);

  if (bStt == LOW && bSttLast == HIGH) {
    bPress = !bPress;
  }

  bSttLast = bStt;
}

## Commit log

2024-10-01 1.10,2024: init commit
    [00_c-mount_insert.stl, 20_Cube_Insert_Beamsplittercube_Base_25x35_v3.stl, 20_Cube_Insert_Beamsplittercube_Dichroicmirror_Retainplate_25_36_v3.stl, 20_Cube_Inse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]
2024-10-18 18.10.2024: SCAD names update
    [10_Base_puzzle_v3.scad, 10_Cube_Lid_1x1_v3.scad, 20_Insert_Lens_holder_v3.scad, 20_Insert_Perpendicular_blank_v3.scad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]
2024-11-27 27.11.2024: README update
    [00_of_sample_holder_v0.stl, 00_of_sample_holder_v1.scad, 00_of_sample_holder_v1.stl, 00_of_sample_plate_v0.scad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]
